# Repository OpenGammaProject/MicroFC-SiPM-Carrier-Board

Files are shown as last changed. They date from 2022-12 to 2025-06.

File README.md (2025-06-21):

# MicroFC SiPM Carrier Board

Carrier board for a 6 mm C-Series MICROFC-60035-SMT silicon photomultiplier by [onsemi](https://www.onsemi.com/pdf/datasheet/microc-series-d.pdf) designed specifically to work with the [Open Gamma Detector](https://github.com/OpenGammaProject/Open-Gamma-Detector), but can be used with any other system. With additional (optional) circuitry for automatic SiPM temperature gain compensation.

PCB size is 18 x 18 mm. The solder pads for the SiPM are slightly bigger than they need to so that you can easily hand-solder everything! You can buy all the parts and the PCB using [Kitspace](https://kitspace.org/opengammaproject/MicroFC-SiPM-Carrier-Board) (non-affiliated).

<p align="center">
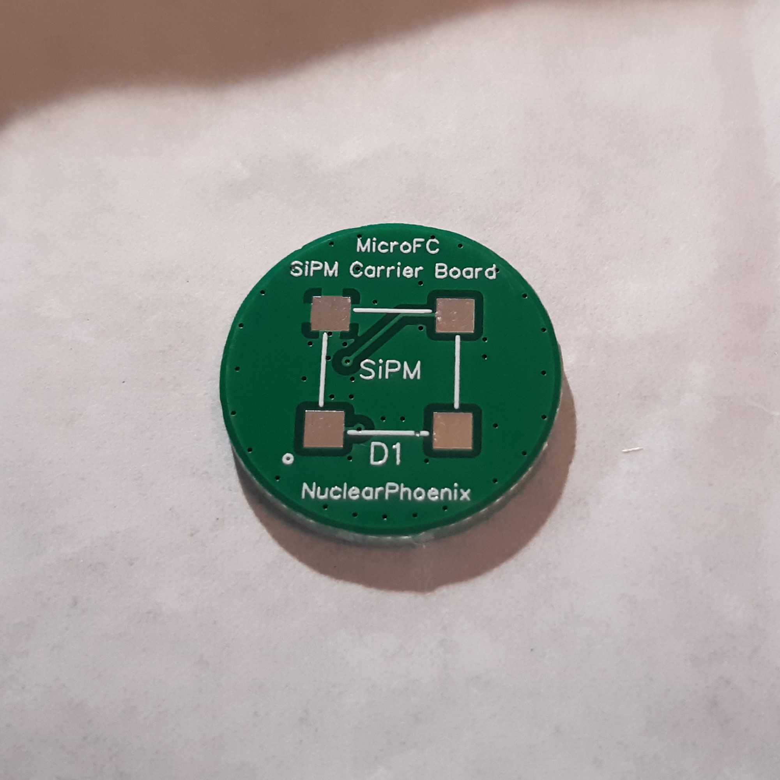
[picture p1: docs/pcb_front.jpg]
Front Side PCB
  
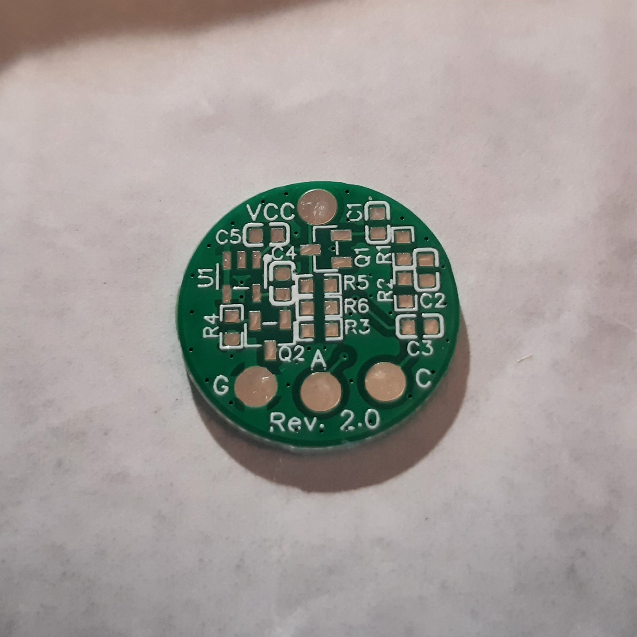
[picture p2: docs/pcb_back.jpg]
Back Side PCB
  
</p>

<p align="center">
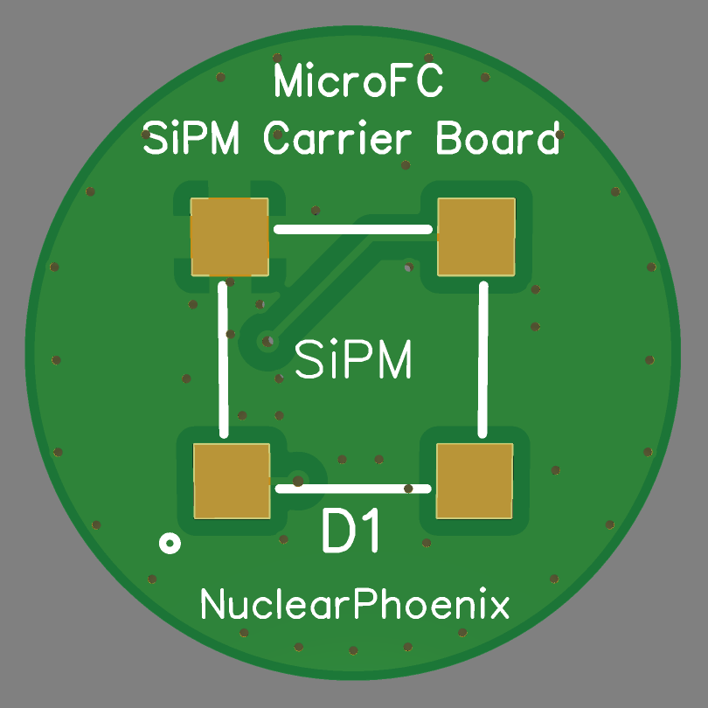
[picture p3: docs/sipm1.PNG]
Front Side PCB Rendering
  
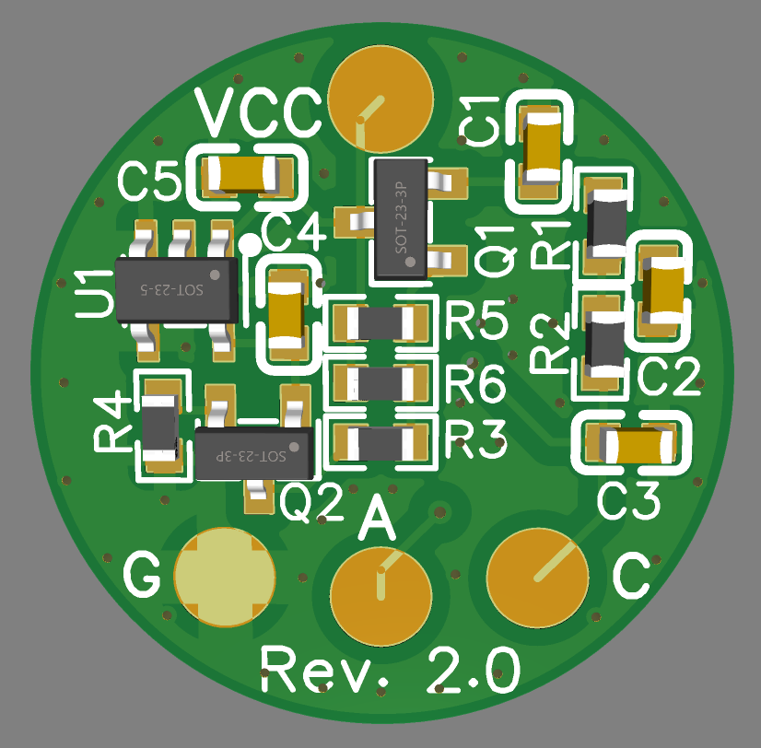
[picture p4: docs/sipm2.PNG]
Back Side PCB Rendering
  
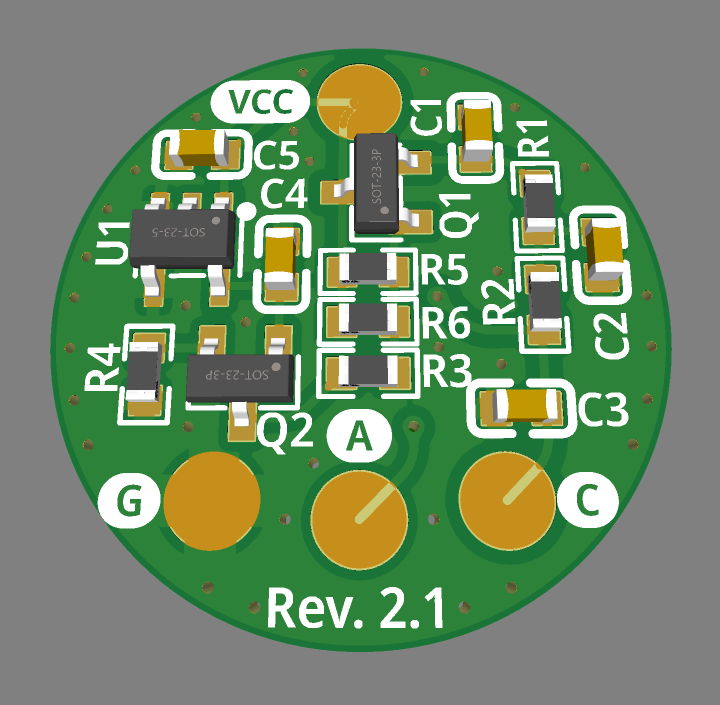
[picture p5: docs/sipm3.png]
Back Side 3D Rendering
  
</p>

On the front side there is only the sensor itself while all the other parts are on the back. This ensures good optical contact and light-tight sealing. The unused SiPM pin number 4 is connected to the ground pad for some added thermal mass and connection to the ground plane where the NTC also sits on.

The PCB includes the recommended SiPM [biasing filter](https://www.onsemi.com/pub/Collateral/AND9782-D.PDF) and temperature compensation that are optional to use. Enable them by soldering all the components on the board and then connect wires to the `VCC` and `GND` pads respectively. The SiPM signal "output" will be anode `A` pad. You can solder an additional wire to the cathode pad `C` in this case, so that you can easily check the voltage that is applied to the SiPM for setting the correct value for example. Do not leave it on there for normal operation though, except if you like antennas on sensitive electronics.

The temperature compensation circuitry is based on a [paper by Evgeny Kuznetsov](https://doi.org/10.1016/j.nima.2017.11.060) (Temperature-compensated silicon photomultiplier). Research and testing was mostly done by [@sebyon](https://github.com/sebyon), thanks a lot!

If you are connecting straight to the SiPM, do so via the cathode `C` and anode `A` pads and leave all the other components unsoldered. You should also use the GND pad in that case too.

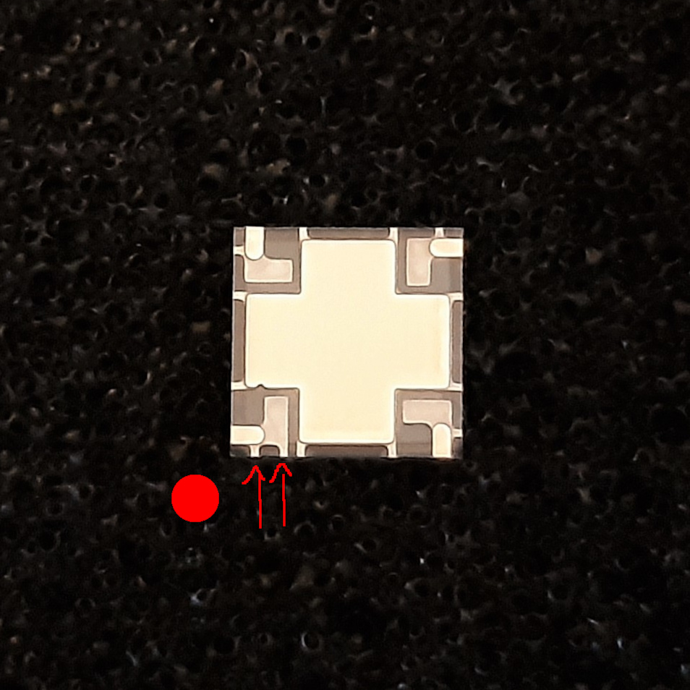
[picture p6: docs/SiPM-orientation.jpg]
SiPM Orientation




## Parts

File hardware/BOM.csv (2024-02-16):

ID | Name | Designator | Footprint | Quantity | Manufacturer Part | Manufacturer | Supplier | Supplier Part | Price
1 | 100nF | C1,C2,C3 | C0603 | 3 | CL10B104KC8NNNC | SAMSUNG(三星) | LCSC | C15725 | 0.008
2 | 2.2uF | C4,C5 | C0603 | 2 | CL10A225KB8NNNC | SAMSUNG(三星) | LCSC | C913904 | 0.023
3 | SiPM | D1 | MICROFC−60035−SMT | 1 |  | ON Semiconductor | Mouser | 863-MFC60035SMTTR1
4 | MMBT5088LT1G | Q1,Q2 | SOT-23-3_L2.9-W1.3-P1.90-LS2.4-BR | 2 | MMBT5088LT1G | onsemi(安森美) | LCSC | C232555 | 0.072
5 | 49.9Ω | R1,R2 | R0603 | 2 | 0603WAF499JT5E | UNI-ROYAL(厚声) | LCSC | C23185 | 0.001
6 | 49.9kΩ | R3,R4 | R0603 | 2 | RT0603BRD0749K9L | YAGEO(国巨) | LCSC | C705780 | 0.025
7 | 24kΩ | R5 | R0603 | 1 | AR03BTCX2402 | Viking(光颉) | LCSC | C319717 | 0.031
8 | 10KΩ | R6 | R0603 | 1 | NTCS0603E3103FLT | VISHAY(威世) | LCSC | C142556 | 0.539
9 | TPS7B6950DBVR | U1 | SOT-23-5_L3.0-W1.7-P0.95-LS2.8-BL | 1 | TPS7B6950DBVR | TI(德州仪器) | LCSC | C174327 | 0.376

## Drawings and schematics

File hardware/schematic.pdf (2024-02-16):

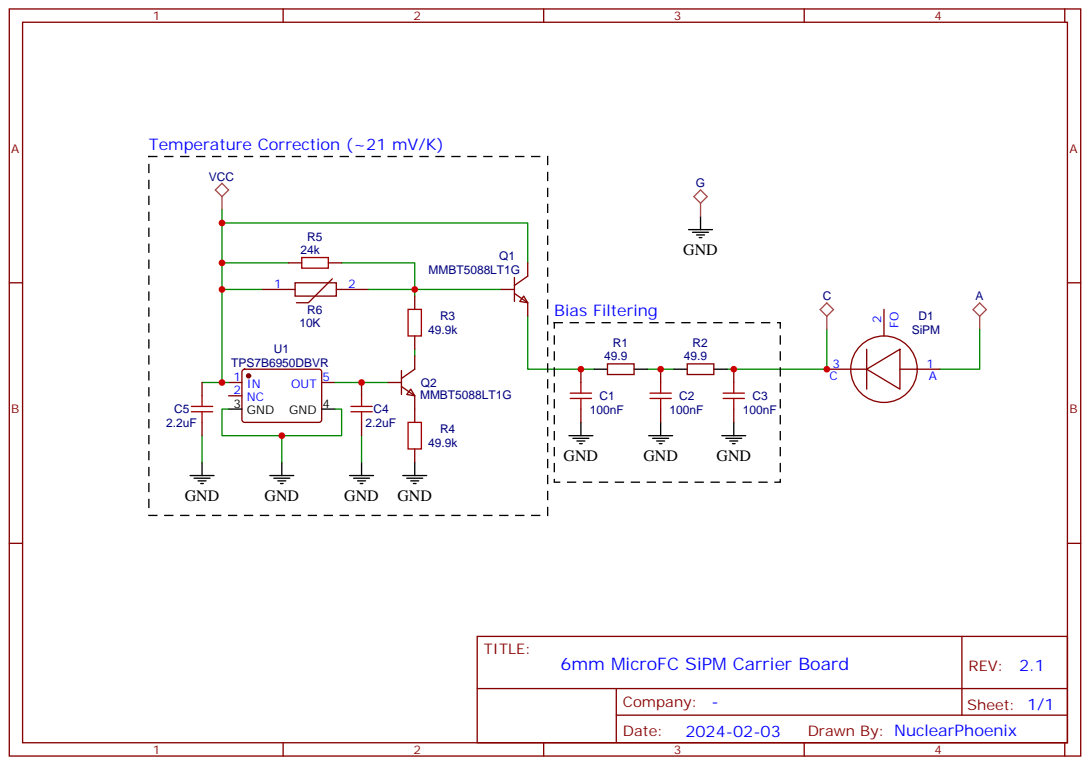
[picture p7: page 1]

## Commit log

2022-05-16 add pcb render images
2022-05-16 add hardware files
    [BOM.csv]
2022-07-08 unzip gerber
    [Drill_PTH_Through.DRL, Gerber_BoardOutlineLayer.GKO, Gerber_BottomLayer.GBL, Gerber_BottomPasteMaskLayer.GBP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]
2022-07-08 convert BOM to UTF-8
    [BOM.csv]
2022-08-01 new revision
    [BOM.csv, Drill_PTH_Through.DRL, Gerber_BoardOutlineLayer.GKO, Gerber_BottomLayer.GBL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]
2022-09-30 rev 1.3
    [BOM.csv, Drill_PTH_Through.DRL, Gerber_BoardOutlineLayer.GKO, Gerber_BottomLayer.GBL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]
2022-09-30 remove pads from BOM
    [BOM.csv]
2023-01-11 Stop filtering out PCB services in kitspace.yaml
2023-07-26 revision 2 boards
    [BOM.csv, Drill_PTH_Through_Via.DRL, Gerber_BoardOutlineLayer.GKO, Gerber_BottomLayer.GBL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]
2023-12-27 [ImgBot] Optimize images
    *Total -- 917.44kb -> 855.40kb (6.76%)
    /docs/pcb_front.jpg -- 465.34kb -> 432.61kb (7.03%)
    /docs/pcb_back.jpg -- 452.10kb -> 422.79kb (6.48%)
2024-02-16 add revision 2.1 files
    [BOM.csv, Drill_PTH_Through.DRL, Drill_PTH_Through_Via.DRL, Gerber_BoardOutlineLayer.GKO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]
2025-02-22 add pick and place file
    [PickAndPlace_PCB.csv]
2025-02-22 update PCB color
2025-12-27 add pcbway project page
